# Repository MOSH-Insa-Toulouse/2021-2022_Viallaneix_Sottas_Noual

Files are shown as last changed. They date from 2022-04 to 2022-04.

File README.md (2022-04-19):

# 2021-2022_Viallaneix_Sottas_Noual MOSH Project 2022
Granulometric sensor

# Informations générales
> Ce projet s'inscrit dans le cadre de l'UF _"Du capteur au banc de test en open source hardware"_.
> Le cœur du projet bat sur la fréquence de la **LOW TECH**. Nous partirons de la fabrication d'un capteur granulométrique élaboré à partir d'une feuille de papier sur laquelle une couche de carbone sera déposée à l'aide d'un crayon à papier (panel de dureté entre HB et 9B) selon un motif prédeterminé. À ce corps d'épreuve, deux électrodes insérées aux extrémités du motif permettront la circulation d'un courant. Une déformation du capteur entraînera une variation du courant mesurable par un système d'acquisition de données. Les enjeux du projet sont donc multiples!
* **Physique** : sur les propriétés d'un capteur granulométrique
* **Technique** : sur la conception et le développement d'un système d'acquisition
* **Exploratoire** : par l'utilisation des outils et concepts de l'Open Source Hardware.
* **Se construire une composante _low-tech_  de l'ingénieur que nous serons** : en s'interrogeant sur les attentes d'une société en mutation, en posant un regard critique sur la notion de progrès technique et sa finalité.

low-tech

# Ce que fait ce projet 

> La finalité du projet est de pouvoir estimer les forces et faiblesses de ces capteurs low-tech. Pour cela nous allons devoir les tester, déterminer leurs caractéristiques et leur limites d'utilisations.
> Pour y parvenir, nous allons concevoir un banc de mesures qui nous permettra, dans un premier temps, d'étalonner les capteurs (leurs sensibilités varient en fonction de la dureté) puis, dans un deuxième temps, de les éprouver dans des conditions et durées d'utilisation controlées.
> Les jeux de données issues de ces tests vont devenir rapidement conséquents et il sera utile de prévoir les scripts et la visualisation en sortie du banc de test et étalonnage. 
> La composante **étalonnage** du banc permet de détérminer la sensibilité un capteur de sensibilité inconnue. La composante **test** permet de soumettre le capteur à des séries de flexion/déflexion fonction d'un angle compris entre -85 et +85 degrés par rapport à la position d'équilibre.
> Dans la suite du projet le capteur désignera le corps d'épreuve et le banc de test permettant l'acquisition des données.

***
## Les axes du projets
* [Présentation du capteur granulométrique](#présentation-du-capteur-granulométrique)
* [Acquisition des données](#acquisition-des-données)
  * [Carte Arduino](#la-carte-arduino)
  * [Étude du circuit électrique](#le-conditionneur)
    * [Partie 1: Mesure d'un très faible courant avec l'aide d'un micro-contrôleur](#partie-1-mesure-dun-très-faible-courant-avec-laide-dun-micro-contrôleur)
       * [Vérification avec la Datasheet de l'AOP](#vérification-avec-la-datasheet-de-laop)
    * [Partie 2: Mise en oeuvre du filtrage du signal](#partie-2-mise-en-oeuvre-du-filtrage-du-signal)
    * [Schéma du circuit électronique final](#schéma-du-circuit-électronique-final)
    * [Partie 3: Simulations sous *LTSpice*](#partie-3-simulations-sous-ltspice)
  * [Code Arduino du système](#code-arduino-du-système)
  * [Application sur Android](#application-sur-android)
* [Réalisation du PCB](#réalisation-du-pcb)
   * [Partie 1: Conception de la schématique et des connexions entre les composants électroniques](#partie-1-conception-de-la-schématique-et-des-connexions-entre-les-composants-électroniques)
   * [Partie 2: Conception du PCB](#partie-2-conception-du-pcb)
   * [Partie 3: Soudure des composants sur le PCB et premiers tests](#partie-3-soudure-des-composants-sur-le-pcb-et-premiers-tests)
* [Banc de tests](#banc-de-tests)
* [Measurement System Analysis](#measurement-system-analysis)
* [Crédits](#auteurs)

***

### Présentation du capteur granulométrique
> Le capteur sélectionné dans le cadre de ce projet est un dépôt de graphite sur un papier, effectué à l’aide d’un crayon plus ou moins gras. 
Nous utiliserons pour cela la résistivité du graphite, qui est suffisamment faible pour laisser circuler un courant mesurable. Néanmoins, avec cette résistivité de 8 µΩ.m (contre 0,017 µΩ.m pour le cuivre), il faudra utiliser un montage amplificateur dans notre banc de test.

> Le dépôt de graphite effectué sur le papier sera alors représentatif de la flexion que ce dernier subit : les grains de graphite jouent le rôle de conducteur mais leur éloignement variera selon la flexion, et va donc influencer la résistance mesurée.

<div align="center">
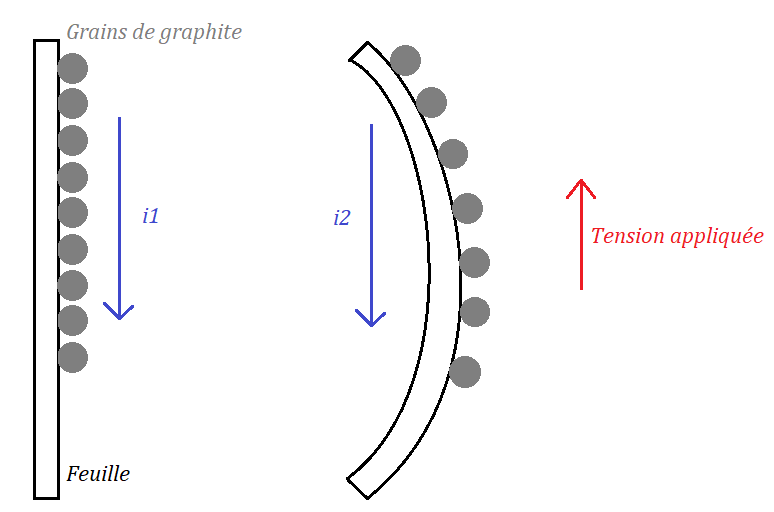
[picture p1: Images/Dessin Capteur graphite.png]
</p>

**Figure 1: Première description schématique d'une mesure sur le capteur de graphite**

<div align="left"></p>

> Dans l’exemple ci dessus, on mesurera pour une même tension appliquée que:

<div align="center">
</p>

<div align="left"></p>

> L’intérêt de ce capteur se situe dans son aspect low-tech qui lui permet d’être facilement produit, mais pas uniquement :  la vaste gamme de dureté des mines de crayon (H, F, HB, B) offre un large choix pour la résistivité du dépôt.
En effet, la dureté d’une mine correspond à ses proportions de graphite et d’argile. Le graphite est, par exemple, plus présent dans un crayon dit « gras » de type B que dans un crayon de type H. Ainsi, nous disposons assez simplement d’un large panel de capteurs pour éventuellement les comparer à l’aide du banc de tests.

(#### Propriété d'un système granulaire)
### Acquisition des données
#### La carte Arduino

Dans notre projet, nous allons utiliser la carte Arduino UNO possédant le microcontrôleur ATMega328. 

<div align="center">
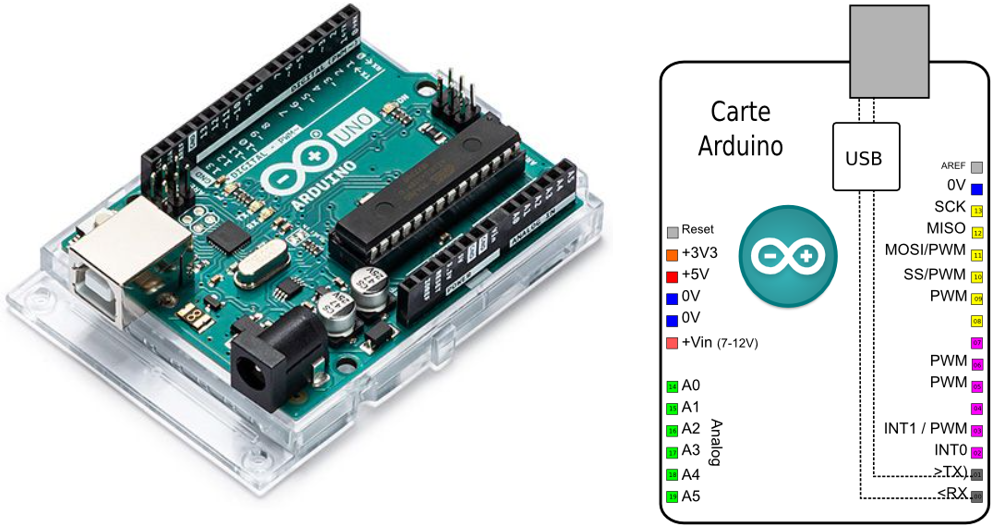
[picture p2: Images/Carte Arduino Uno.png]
</p>

**Figure 2: Illustration de la carte Arduino UNO et Brochage de la carte Arduino**

<div align="left"></p>

Elle dispose de 6 entrées analogiques et de 14 broches numériques d'entrées/sorties. 
Pour pouvoir l'utiliser, on a juste à la connecter directement à l'ordinateur via le câble USB. 

La carte Arduino UNO possède les caractéristiques suivantes: 

* **Résolution**: 10 à 12 bits (1024 à 4096 points)
* **Pleine échelle (VRef)**: de 1.1 V à 5.0 V
* **Impédance de source max**: 1 kΩ à 10 kΩ
* **Fréquence d'échantillonnage**: 15 kHz maximale

#### Le conditionneur

#### Partie 1: Mesure d'un très faible courant avec l'aide d'un micro-contrôleur
L’objectif étant d’extraire l’information utile du capteur ayant un très faible courant (environ 100 nA), le montage électrique doit être adapté de manière à mesurer des courants faibles. Selon les caractéristiques techniques du microcontrôleur Arduino (cf Datasheet), on ne peut pas mesurer directement de très faibles courants en raison de l’impédance de source (environ égale à quelques kOhms). Il est donc nécessaire d’utiliser un circuit amplificateur transimpédance composé d’un amplificateur opérationnel AOP pour convertir un courant issu du capteur en une tension mesurable par le CAN (Convertisseur Analogique-Numérique) de l’Arduino UNO.

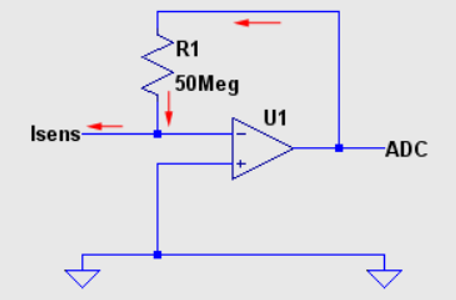
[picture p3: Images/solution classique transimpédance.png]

<div align="center"></p>
  
**Figure 3: Montage de transimpédance (ou convertisseur courant-tension)**
  
<div align="left"></p>

L’inconvénient d’un montage classique de transimpédance est qu’il nécessite une grande résistance pour amplifier le signal et que la tension d’alimentation du capteur doit être négative. On peut donc ajouter un autre étage inverseur à la suite du premier montage : 

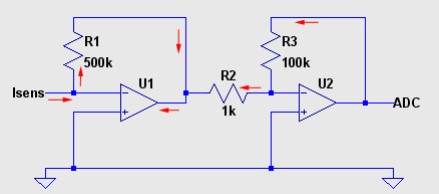
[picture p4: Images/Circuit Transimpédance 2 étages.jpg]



<div align="center"></p>
  
**Figures 4 et 5: Ajout d'un étage inverseur sur le montage de transimpédance et Calcul du gain du second montage**

<div align="left"></p>

Dans le montage ci-dessus, le gain du second étage étant négatif compte-tenu de son caractère inverseur (`cf Figure 3`), la résistance R1 du premier étage n’a plus besoin d’avoir une grande valeur. De plus, l’alimentation du capteur est donc positive grâce au second montage inverseur du fait des produits des gains de deux étages. 

Pour plus de simplicité, on a choisi un montage en prenant un seul AOP dans le montage.
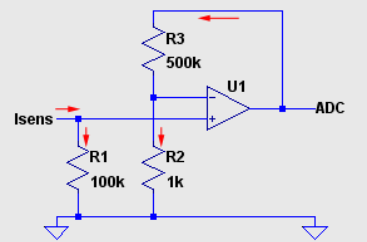
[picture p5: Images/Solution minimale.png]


<div align="center"></p> 

**Figure 6: Solution simplifiée pour le montage transimpédance**



**Figure 7: Calcul de la tension aux bornes de R1**

<div align="left"></p>
  
En calculant la tension aux bornes de la résistance R1, on obtient une tension environ égale à 10 mV d'après la `Figure 4`.

Il s’agit d’une valeur importante pour le choix de l’AOP notamment pour l'effet de l’offset du signal d’entrée. 
Le Gain de ce montage et la Tension de sortie ADC sont décrits dans les calculs ci-dessous : 




<div align="center"> </p>
  
**Figure 8: Calculs du gain du montage et de la tension de sortie**

<div align="left"></p>
  
Si on a un courant nul en entrée, on veut alors obtenir une tension ADC nulle en sortie, cela implique qu’il n’y ait pas de dérives en tension de la part de l’AOP.
Les principales contraintes pour le choix de l’amplificateur opérationnel sont le faible courant d’entrée et un très faible offset de tension devant être négligeable devant 10mV (tension aux bornes de R1).

##### Vérification avec la Datasheet de l'AOP

Selon les données de la [Datasheet](LTC1050C.pdf) de l'AOP 1050C, on constate qu'il possède un faible offset de tension d'environ 5μV au maximum et un très faible drift pour l'offset de tension à environ 0.05μV/°C. Cela indique la bonne stabilité de l'amplificateur opérationnel. Par comparaison, les AOP utilisés traditionnellement en salle de TP possèdent un offset autour de 5mV, une valeur 1000 fois plus grande que celle du 1050C.
En comparant la tension d'entrée (autour de 10mV `cf Figure 5`), on constate que l'offset de 5μV est très faible.
De plus, on peut remarquer que cet AOP possède un mode commun incluant la masse ce qui correspond à notre montage électrique.
  
<div align="center"></p>
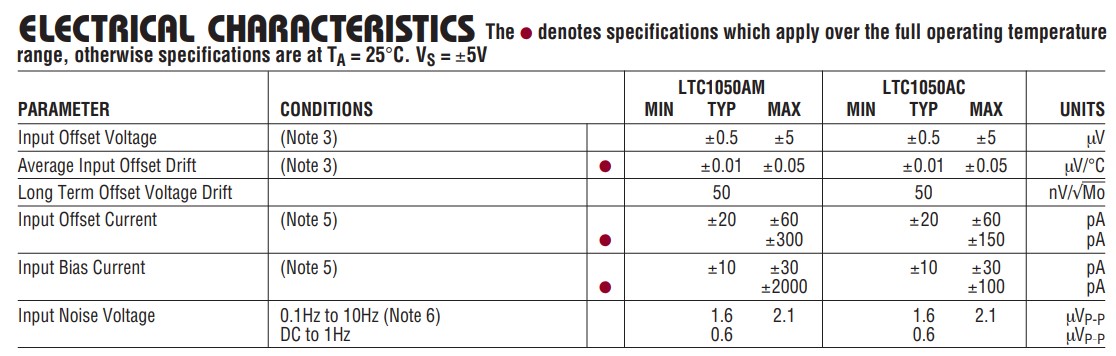
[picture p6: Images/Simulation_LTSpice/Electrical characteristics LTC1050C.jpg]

  
**Figure 9: Extrait de la datasheet dans la partie Electrical Characteristics**

<div align="left"></p>
  
Enfin, on constate que le courant de polarisation en entrée (Input Bias Current) est au maximum égale à 30pA, cela convient car nous effectuons des mesures de courant autour de 100nA. Il faut que le courant Isense `cf Figure 4` soit très faible devant 100nA et le reste du courant passe dans la résistance R1. 
En respectant les différentes conditions énoncées précédemment, l'AOP 1050C est adapté pour notre circuit électronique.

#### Partie 2: Mise en oeuvre du filtrage du signal

Étant donné que ce montage est très sensible aux signaux parasites (50Hz, horloge du microcontrôleur Arduino, Bluetooth entre autres), on doit mettre en œuvre un filtrage passe-bas pour limiter les perturbations du signal.
D’une part, il faut appliquer un filtre passif en entrée pour limiter les perturbations de type radiofréquences pouvant conduire à un excès de bruit dans l’ADC.
Ensuite, on applique un filtre actif au niveau de l’amplificateur opérationnel pour augmenter l’efficacité de l’échantillonnage du signal. 
À la sortie de l’AOP, on utilise un dernier filtre passif pour retirer le bruit sur le traitement du signal et les phénomènes de repliement de spectre (aliasing). 

En intégrant les différents filtres, le montage ressemble à ceci : 

<div align="center"></p>
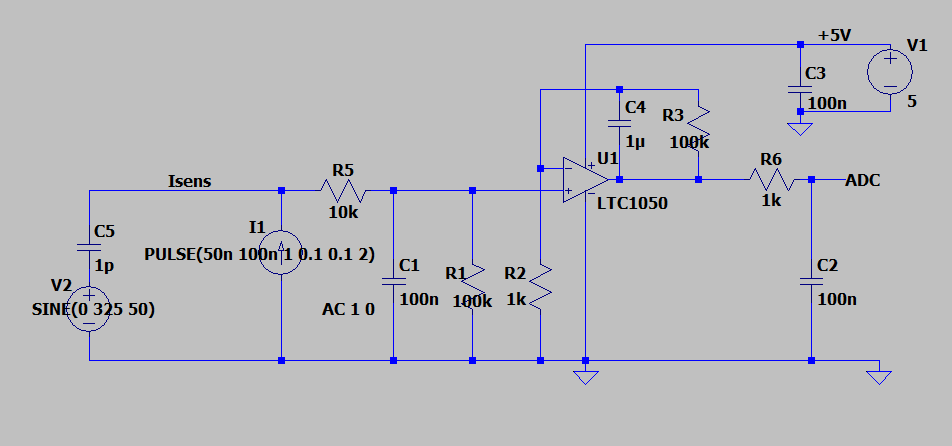
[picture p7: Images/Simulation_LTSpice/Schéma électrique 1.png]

  
**Figure 10: Schéma du montage électrique avec les différents filtres**

<div align="left"></p>

On distingue 3 différents filtres où nous avons cherché pour chacun la fréquence de coupure et son rôle principal pour le filtrage : 

<div align="center"></p>
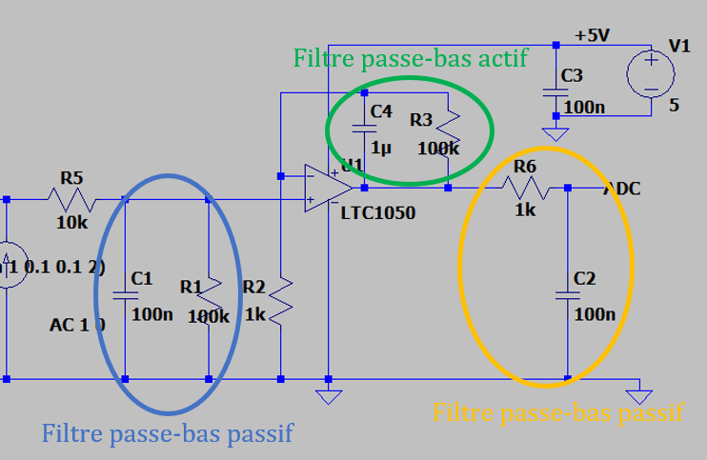
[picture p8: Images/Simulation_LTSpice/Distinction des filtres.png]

  
**Figure 11: Identification des différents filtres dans le montage**

<div align="left"></p> 
 
Tout d'abord, le filtre passe-bas passif, placé à l'entrée de l'AOP, est constitué de R1(100kΩ) et C1(100nF). Il possède une fréquence de coupure théorique environ égale à 16Hz `cf Figure 7` . Il permet donc de filtrer les perturbations et les excès de bruit en courant sur la forme du signal d'entrée. 


<div align="center"></p> 

**Figure 12: Calcul de la fréquence de coupure du filtre passif (R1 et C1)**

<div align="left"></p>

Ensuite, le filtre passe-bas actif, placé entre l'entrée et la sortie de l'AOP, est constitué de R3(100kΩ) et C4(1μF) en parallèle. Ce dernier possède une fréquence de coupure théorique environ égale à 1.6Hz `cf Figure 8`. Son rôle principal est de supprimer la composante parasite de 50Hz (du fait du couplage capacitif avec la tension 230V) qui perturbe significativement le signal `cf Figure XX`.


<div align="center"></p>

**Figure 13: Calcul de la fréquence de coupure du filtre actif (R3 et C4)**

<div align="left"></p>

Enfin, le filtre passe-bas passif, placé à la sortie de l'AOP, est constitué de R6(100kΩ) et C2(100nF). Il possède une fréquence de coupure théorique environ égale à 1.6kHz `cf Figure 9`. En sachant que la fréquence d'échantillonnage du micro-contrôleur est environ égale à 15,4kHz, il faut respecter la condition d'échantillonnage de Shannon à savoir:  

<div align="center"></p> 

</p>
</p>
</p>

**Figures 14: Calcul de la fréquence de coupure du filtre passif (R6 et C2) et Vérification de la condition d'échantillonnage de Shannon**

<div align="left"></p>

Selon les calculs, on respecte bien la condition d'échantillonnage de Shannon `cf Figure ci-dessus`, le filtre permet de limiter les effets de repliement de spectre (rôle d'anti-aliasing) et de manière générale, le bruit lors du traitement du signal. 

#### Schéma du circuit électronique final
> Voici un première proposition du schéma électrique
  
<div align="center"></p>


**Figure 15: Premier schéma du montage électronique**

<div align="left"></p>
  
Dans ce schéma, nous simulons le bruit en courant à l'entrée en mettant une capacité à côté du générateur de tension. On a ajouté une capacité C3 pour filtrer le bruit de la source d'alimentation.
  
> On propose une optimisation du montage électronique en simulant le capteur de graphite `cf Figure ci-dessous`
  
<div align="center"></p>
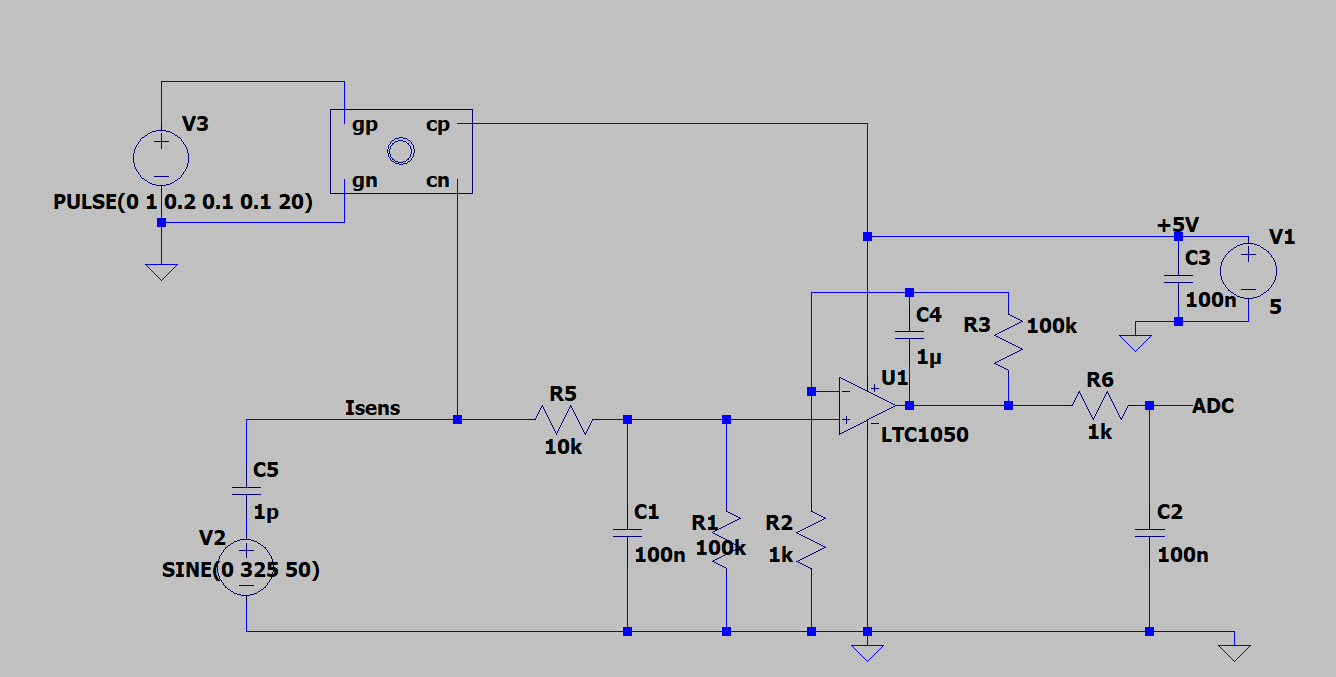
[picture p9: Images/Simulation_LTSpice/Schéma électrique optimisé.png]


**Figure 16: Schéma électrique optimisé**

<div align="left"></p>
  
Nous avons simulé notre capteur de graphite (cf rectangle en haut à gauche de la `figure précédente`). 
> Commentaires à ajouter

#### Partie 3: Simulations sous *LTSpice*
  
On vérifie les conditions optimales de fonctionnement du montage électronique en effectuant différentes simulations sur le logiciel *LTSPice* `cf figures ci-dessous`.

<div align="center"></p>
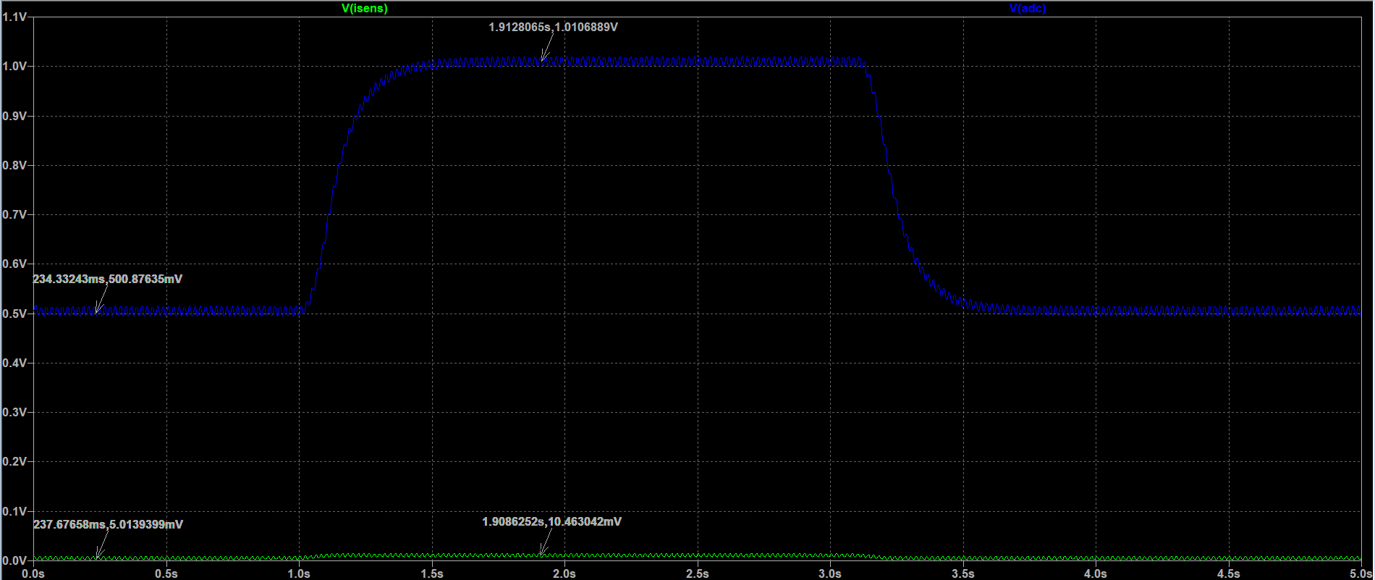
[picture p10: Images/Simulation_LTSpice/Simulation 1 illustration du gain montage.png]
</p>

**Figure 17: Vérification du gain d'amplification du signal environ égal 100**
  
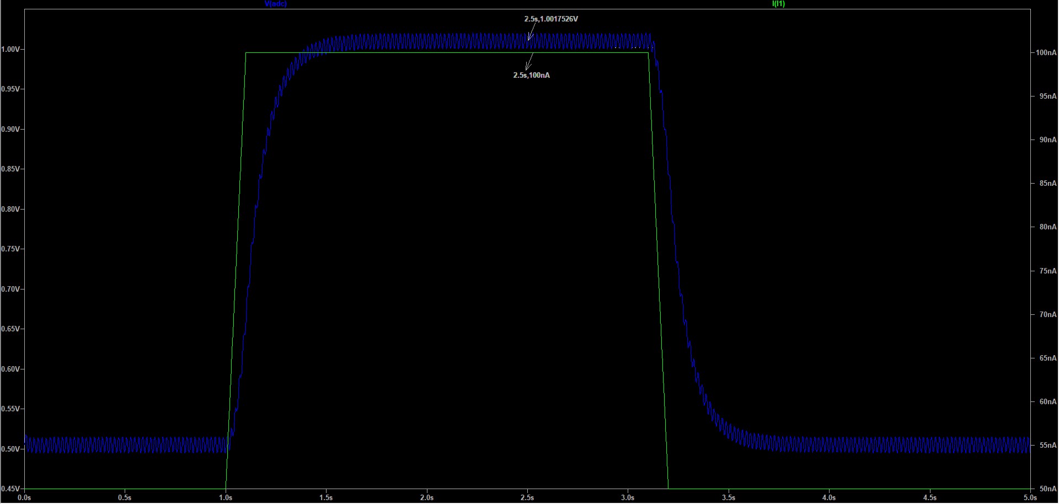
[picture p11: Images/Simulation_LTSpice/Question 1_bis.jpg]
</p>

**Figure 18: Vérification du la tension de sortie du montage avec un courant d'entrée égal à 100nA**

<div align="left"></p>
  
Pour l'illustration graphique du gain du montage général, on distingue qu'il y a bien 3 filtres dans le circuit électronique grâce aux différentes variations du terme de phase (courbe en traits en pointillés `cf Figure ci-dessous`).

<div align="center"></p>
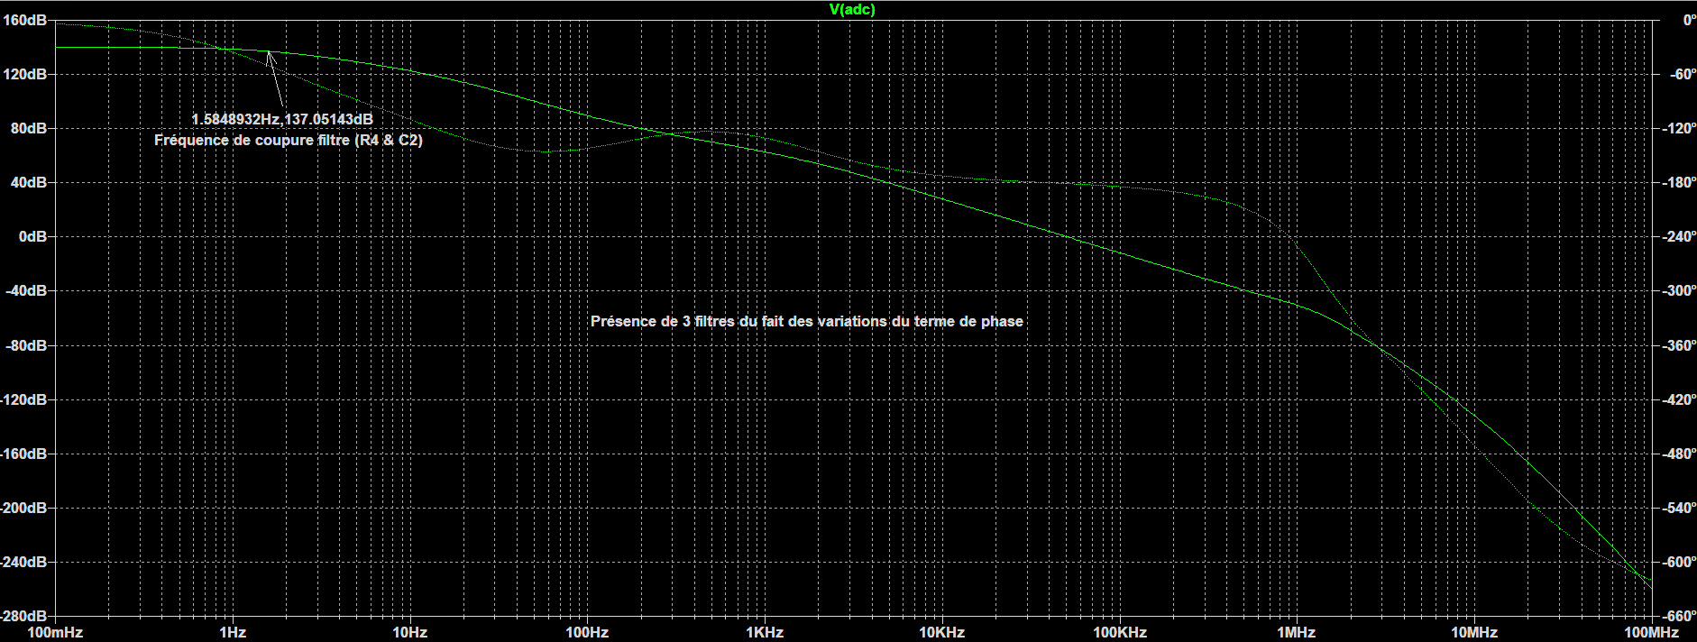
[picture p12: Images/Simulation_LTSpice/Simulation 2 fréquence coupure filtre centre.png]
</p>

**Figure 19: Identification graphique des 3 filtres**

<div align="left"></p>

> On vérifie graphiquement la fréquence de coupure de chaque filtre en effectuant une simulation fréquentielle (AC Sweep):

Pour le premier filtre à l'entrée de l'AOP (R1 et C1):
<div align="center">
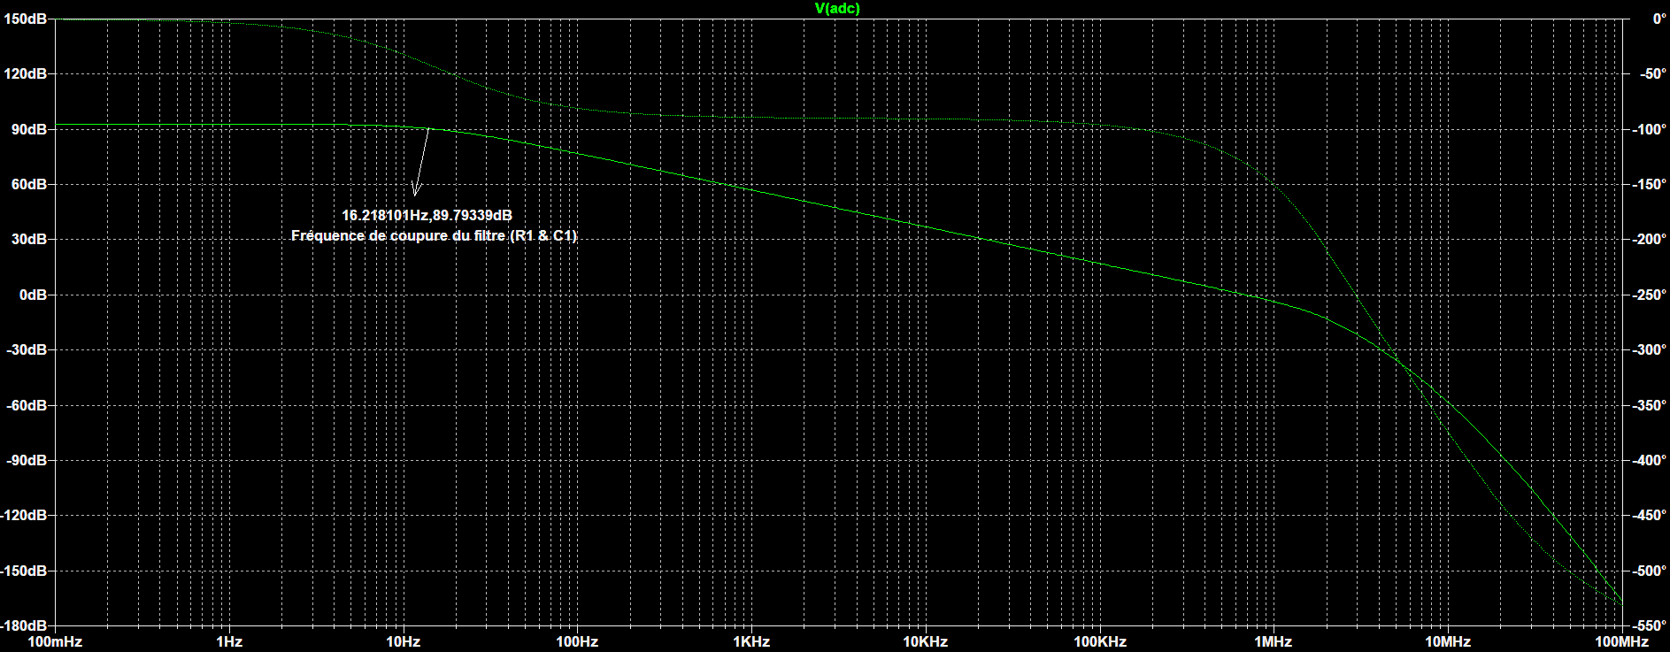
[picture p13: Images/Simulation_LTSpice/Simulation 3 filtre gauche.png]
</p>

**Figure 20: Illustration graphique de la fréquence de coupure du filtre (R1 et C1)**

<div align="left"></p>
  
Pour le second filtre entre l'entrée et la sortie de l'AOP (R3 et C4) et le dernier filtre à la sortie (R6 et C2):
  
<div align="center">
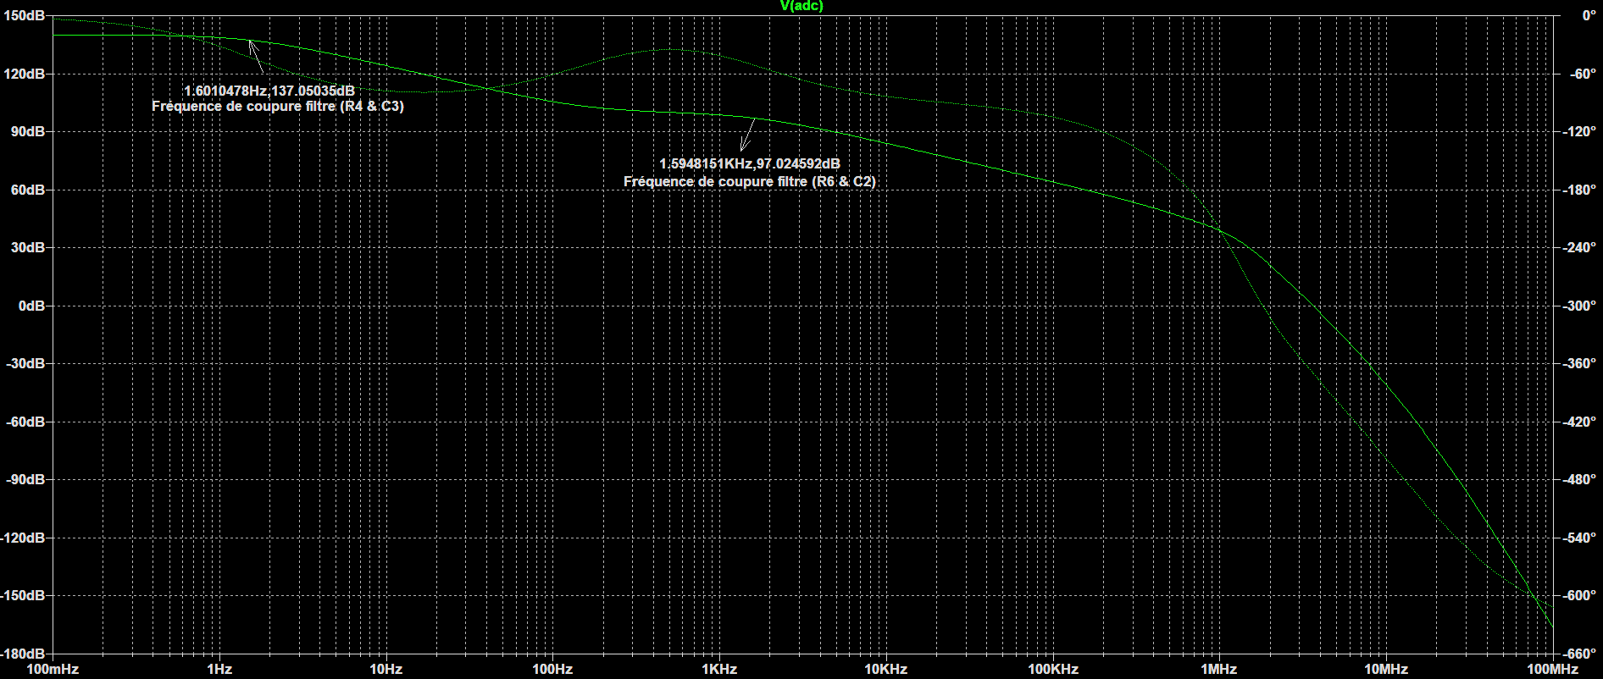
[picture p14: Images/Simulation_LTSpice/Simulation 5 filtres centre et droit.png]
</p>

**Figure 21: Illustration graphique des fréquences de coupure des deux filtres passe-bas**

<div align="left"></p>

> On vérifie l'incidence du courant d'entrée de l'amplificateur sur la tension de sortie par une simulation temporelle:

<div align="center">
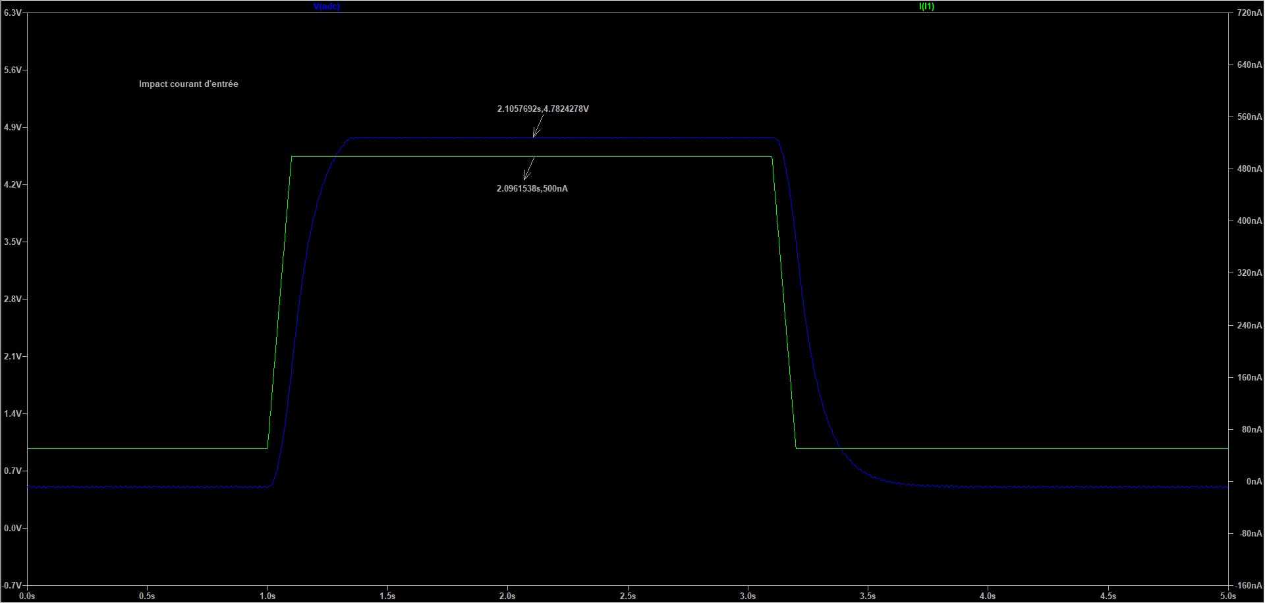
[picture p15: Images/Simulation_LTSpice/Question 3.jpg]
</p>

**Figure 22: Illustration graphique de l'incidence du courant d'entrée sur la tension de sortie**

<div align="left"></p>
  
On peut remarquer dans cette image qu'à partir d'une valeur de 500nA pour le courant d'entrée, on obtient une tension pouvant saturer le convertisseur analogique-numérique de l'Arduino. 

> On observe graphiquement l'atténuation globale du signal d'un bruit en courant de 50 Hz ainsi que celle associée à un bruit en courant à la fréquence de repliement de spectre autour de 7 kHz. 

<div align="center">
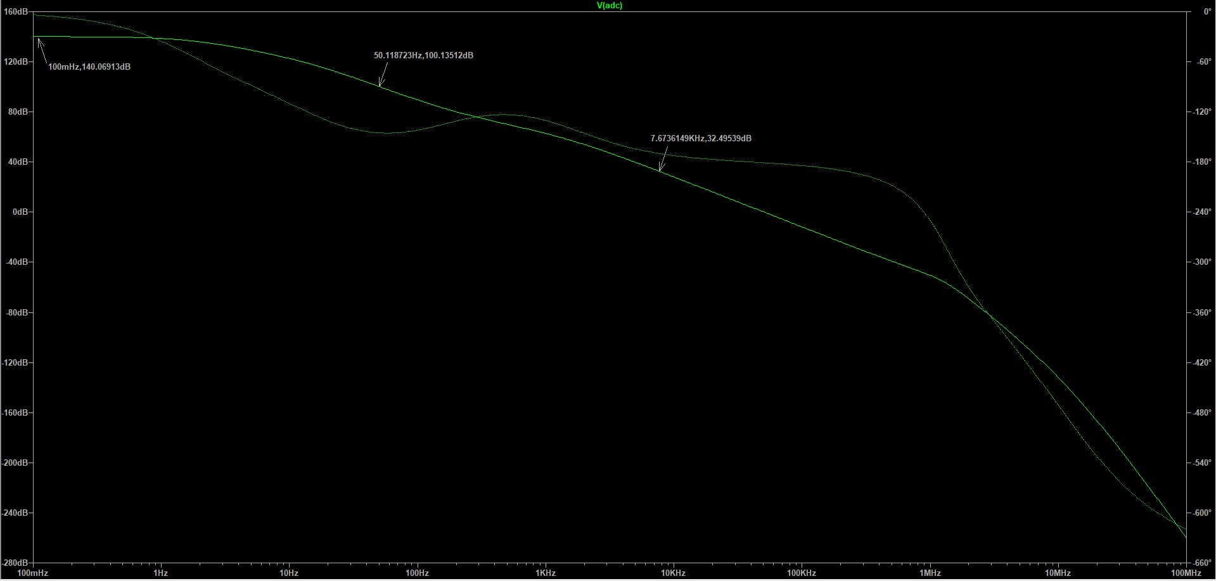
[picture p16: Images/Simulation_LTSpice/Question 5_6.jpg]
</p>
 


**Figures 23 et 24: Illustration graphique de l'atténuation du signal d'un bruit en courant pour deux fréquences spécifiques et calculs des atténuations**

<div align="left"></p>

Comme on peut le voir avec les calculs précédents, on constate qu'il y a une atténuation en bruit de courant environ égale à 40dB pour une fréquence autour de 50Hz et elle est environ égale à 100 dB pour un bruit en courant au voisinage de la fréquence de repliement de spectre. Cela montre bien que le signal peut être fortement perturbé et atténué si on laisse la composante fréquentielle à 50 Hz et si on ne respecte la condition d'échantillonnage.   

### Code Arduino du système
<div align="center">
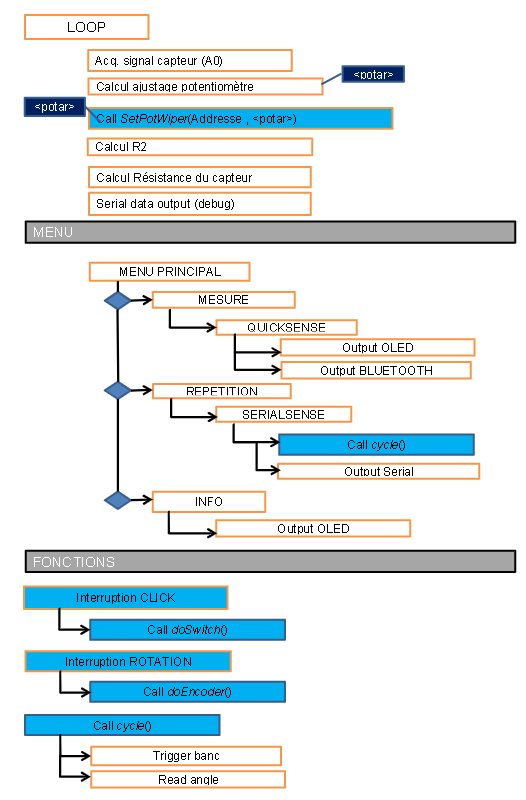
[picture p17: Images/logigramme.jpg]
</p>

**Figure 25: Logigramme de notre code Arduino**

<div align="left"></p>
  
Voici une présentation graphique de notre code Arduino.
  
### Application sur Android

L'application mobile associée au banc de test fonctionne avec un timer identique à celui du programme Arduino. L'utilisateur peut se connecter au module Bluetooth de son choix, puis vérifie que la connexion est bien établie avec un second bouton. Il peut ensuite lancer la mesure et afficher les résultats reçus sur un graphe en temps réel, afin de suivre l'évolution de la résistance du capteur. Le graphe reprend du début lorsque le balayage atteint le bout de l'écran, mais l'utilisateur peut le réinitialiser à sa guise avec un autre bouton. Enfin, la mesure peut être arrêtée en appuyant à nouveau sur le bouton qui l'a déclenché.

<div align="center"></p>
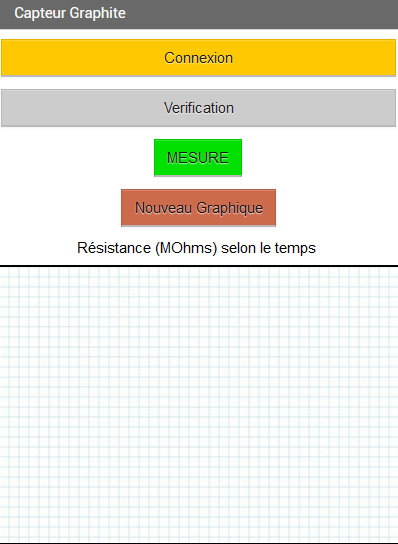
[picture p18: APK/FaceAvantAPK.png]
</p>

**Figure 26: Aperçu visuel de notre application**

<div align="left"></p>

<div align="center">
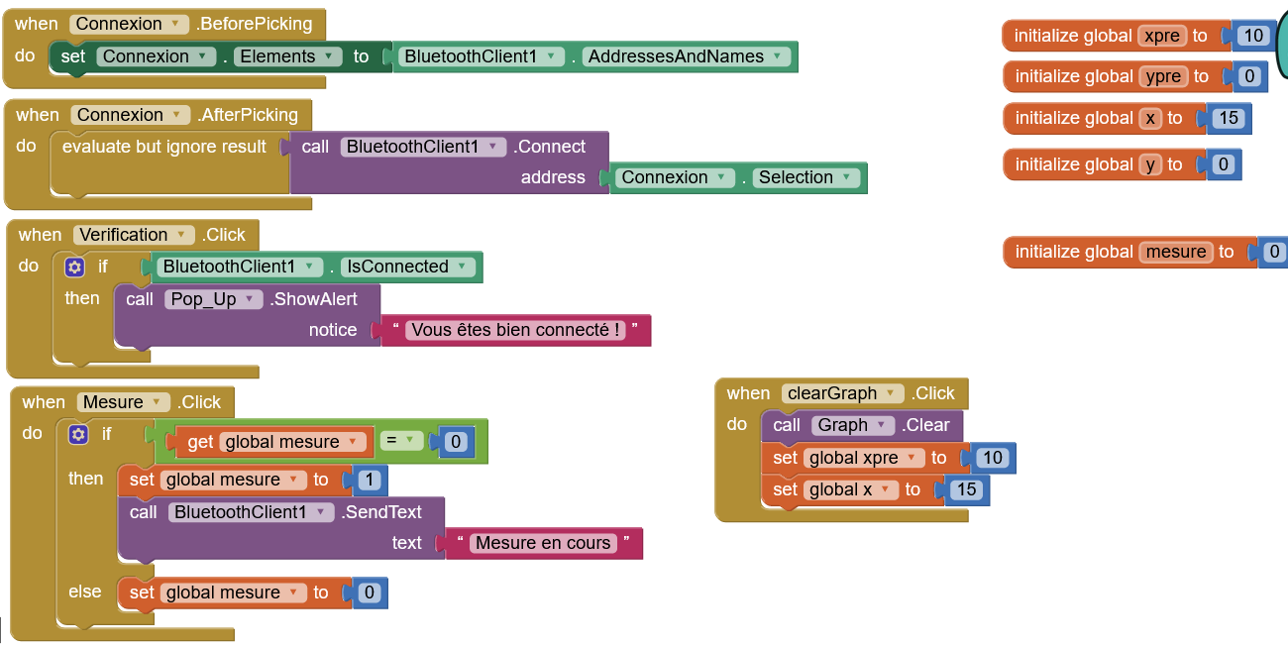
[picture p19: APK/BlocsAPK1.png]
</p>
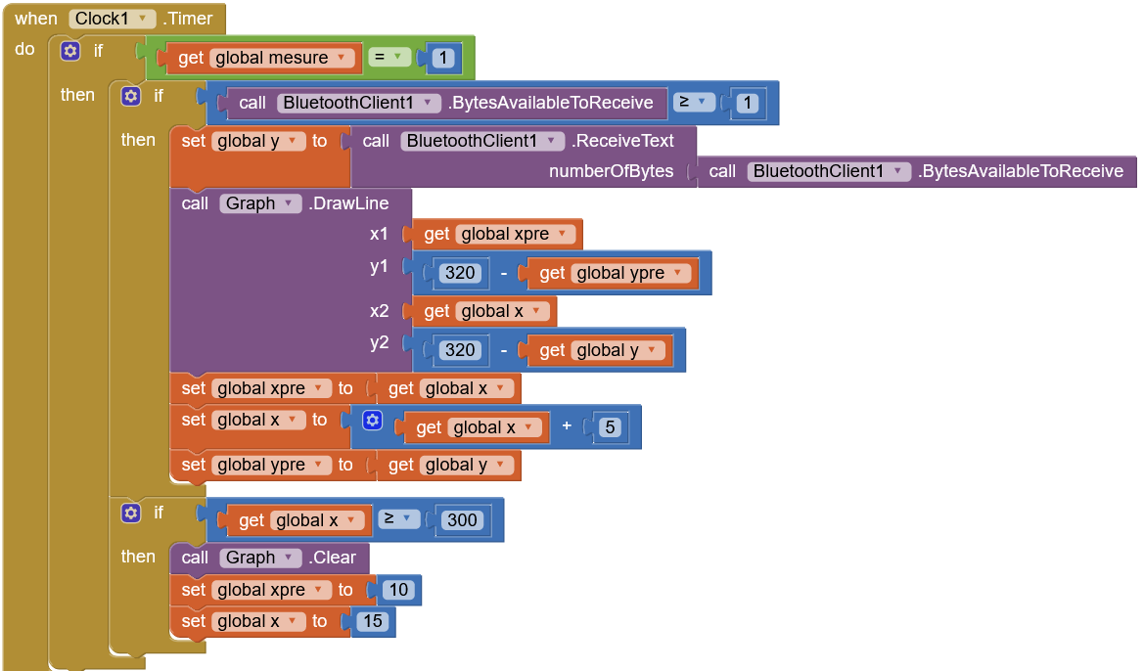
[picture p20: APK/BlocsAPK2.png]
</p>

**Figures 27 et 28: Extraits des blocs pour la réalisation de l'application Android sur *MIT App Inventor***

<div align="left"></p>   

### Réalisation du PCB

Après avoir réalisé les simulations sur *LTSpice*, nous avons conçu un premier modèle de PCB avec l'aide du logiciel *KiCAD*. 

#### Partie 1: Conception de la schématique et des connexions entre les composants électroniques

> Lors de cette étape, nous avons choisi un modèle basé sur l'Arduino UNO pour avoir les bonnes dimensions de la carte et les pins de connexion adéquats. Afin de réaliser précisément le PCB, nous avons dû concevoir certains composants électroniques nous-mêmes dans la partie Schématique (écran OLED, module Bluetooth, l'amplificateur LTC1050C, l'encodeur rotatoire et le potentiomètre digital)  `cf Figures ci-dessous`

<div align="center">
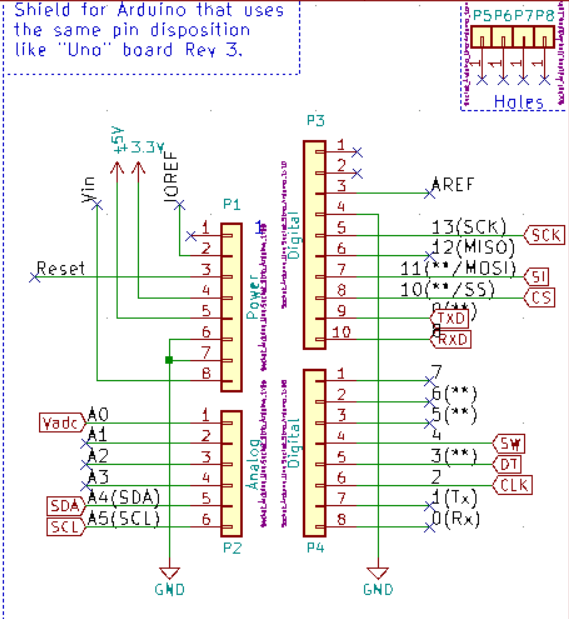
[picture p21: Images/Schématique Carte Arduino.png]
</p>

**Figure 29: Schéma des pins de connexion de la carte Arduino UNO **

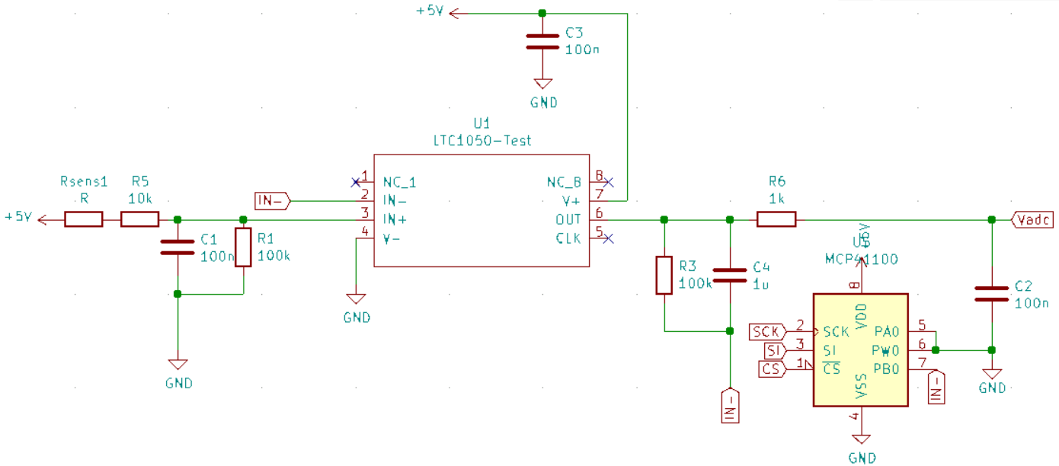
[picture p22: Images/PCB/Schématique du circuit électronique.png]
</p>
 
**Figure 30: Schéma du circuit électronique**
 
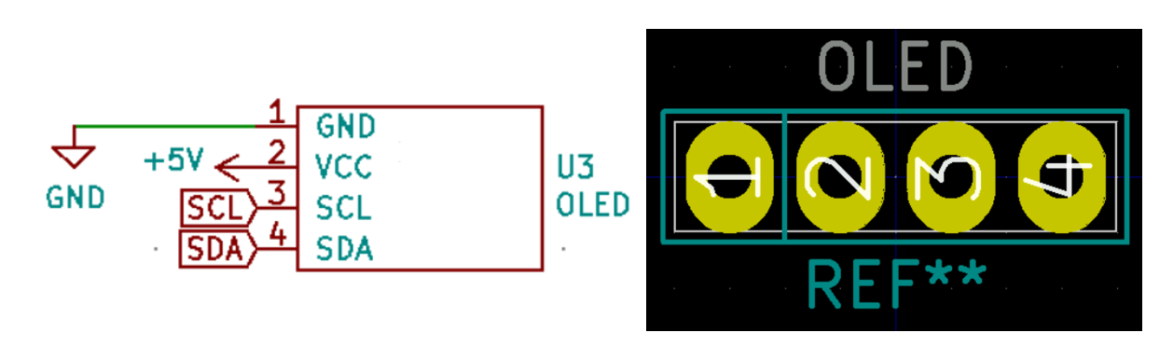
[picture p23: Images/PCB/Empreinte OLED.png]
</p>
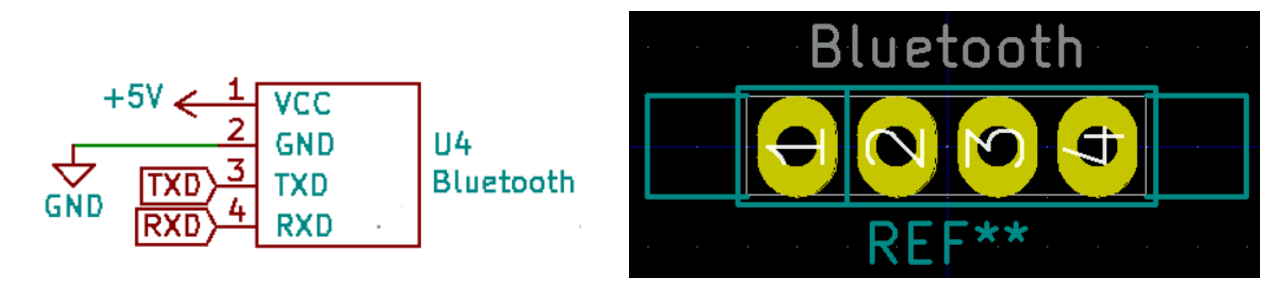
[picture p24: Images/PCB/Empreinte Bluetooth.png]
</p>
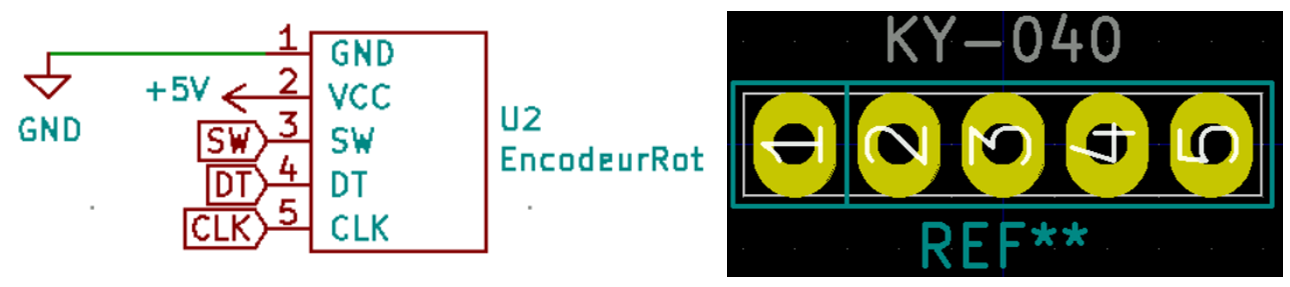
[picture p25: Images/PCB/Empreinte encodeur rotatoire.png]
</p>
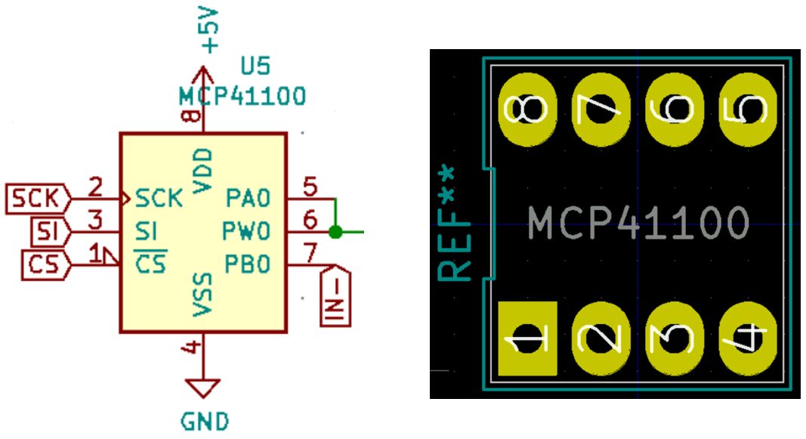
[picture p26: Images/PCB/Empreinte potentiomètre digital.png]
</p>

**Figures 31: Schémas et empreintes de chacun de nos composants électroniques (Écran OLED, BLuetooth, Encodeur rotatoire, Potentiomètre digital)**

<div align="left"></p>

#### Partie 2: Conception du PCB

> Dans cette partie, nous plaçons virtuellement les différents composants sur le PCB et nous effectuons toutes les connexions entre les pins de composants et ceux de la carte Arduino. Nos différents professeurs réferents (Mr Jérémie Grisolia et Mme Catherine Crouzet) nous ont indiqués les consignes à respecter pour la réalisation du PCB: 
  
* Largeur des pistes = 0.6 mm
* Largeur d'isolation des pistes = 0.9 mm
* Dimensions du trou pour l'écran OLED, le module Bluetooth et l'encodeur rotatoire = 2 mm * 2.5 mm
* Diamètre du via (trou entre la face avant et arrières du PCB) = 2 mm
* Taille du trou de perçage du via = 0.8 mm
* Taille du trou de perçage pour l'écran OLED, le module Bluetooth et l'encodeur rotatoire, l'AOP et le potentiomètre digital = 1 mm
* Dimensions du trou pour le support de l'AOP (pad n°1 rectangulaire et les autres pins sont ovales) = 2 mm * 2.5 mm
* Taille du trou de perçage pour les résistances et les capacités = 0.8 mm
  
<div align="center">
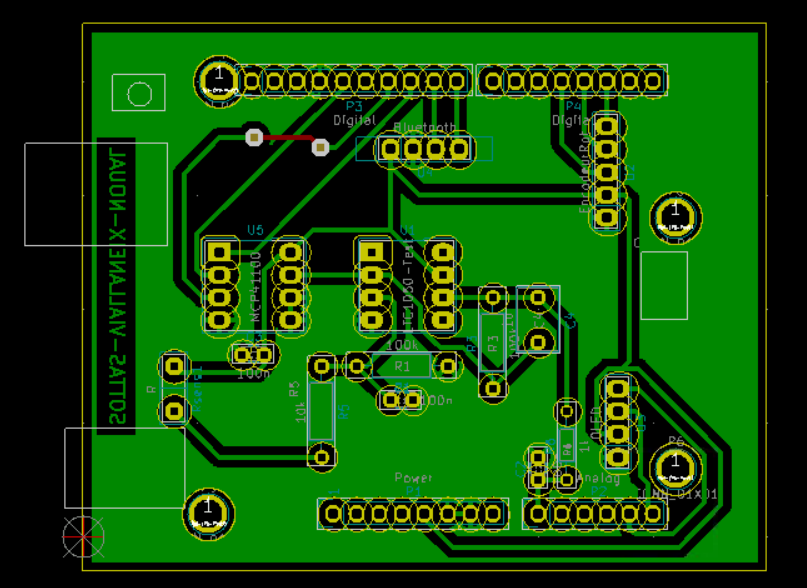
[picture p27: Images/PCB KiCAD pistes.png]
</p>

**Figure 32: Schémas des pistes sur le PCB**

<div align="left"></p>

<div align="center">
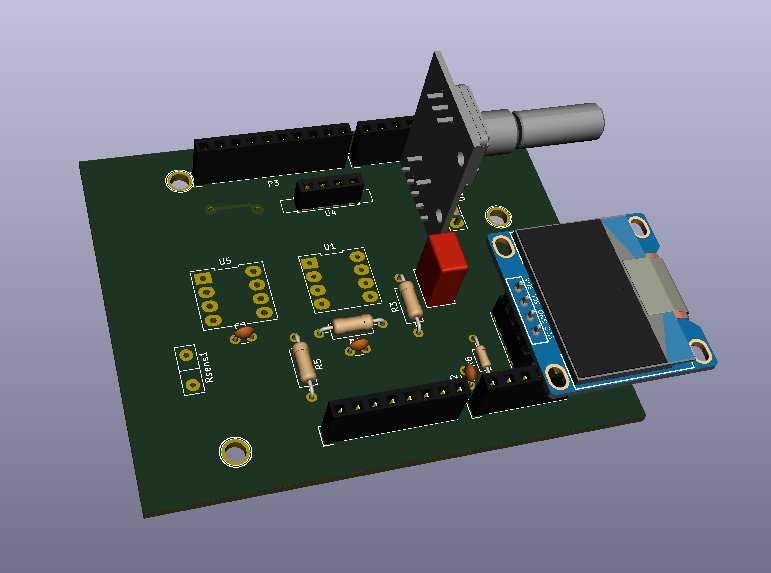
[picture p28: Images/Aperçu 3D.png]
</p>

**Figure 33: Schéma 3D des pistes sur le PCB**

<div align="left"></p>
  
Avec l'aide de Mme Catherine Crouzet, nous avons réalisé le PCB selon le protocole suivant:

* Insolation de la plaque de résine positive par photo-lithographie UV par contact avec un masque `cf Figure ci-dessous` imprimé sur un film transparent, provenant du logiciel *KiCAD*. Cette résine est choisie de telle manière à être sensible aux rayons UV.
Une fois l'insolation réalisée, la partie de la résine insolée est dissoute dans une solution de développeur. Le reste de la résine, étant protégé par le masque, reste intact. On observe l'apparition des pistes du circuit sur le PCB.
  
* Passage dans un bain de péroxyde de fer pour enlever les résidus de la piste de cuivre sur le PCB
  
* Nettoyage et Séchage de la plaque à l'eau naturelle

<div align="center">
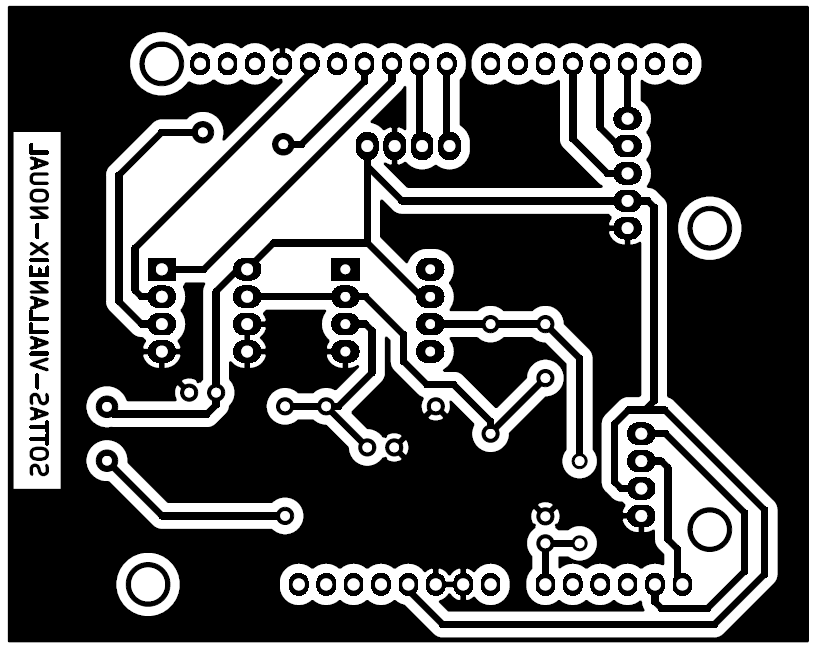
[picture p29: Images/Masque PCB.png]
</p>

**Figure 34: Masque imprimé du PCB sur un film transparent**

<div align="left"></p>

#### Partie 3: Soudure des composants sur le PCB et premiers tests
 
Uns fois le PCB réalisé, nous avons percé tous les trous des pins associés à chaque composant électronique puis nous avons soudé les différents composants et les broches latérales entre le PCB et la carte Arduino.

### Banc de tests

> Le but de ce banc de test est de déterminer la sensibilité du capteur, de voir l’évolution de cette dernière selon la répétition des flexions et de comparer ces données avec un capteur commercialisé "Flex-Sensor".

> Ce banc de test est composé d’un servomoteur pour une bonne précision sur les angles, ainsi que d’un support où l’on vient encastrer le capteur. Une roue où l’on positionne le bout du capteur est alors entraînée par le servomoteur et génère la flexion. Il est fait de plaques de contreplaqué superposées, qui ont été découpées au FabLab et il permet de garder le capteur le plus intact possible, car celui-ci n’est maintenu qu’aux deux extrêmités et non pas sur le dépôt de graphite lui-même.
L’utilisateur détermine au préalable le nombre de répétitions souhaité à l’aide de l’encodeur rotatoire placé sur le PCB. Il peut ensuite récupérer les données (angle, itération de la mesure, résistance lue) sur le moniteur série et les traiter dans un logiciel comme Rmarkdown, Python via l'interpréteur Spyder IDE ou Qtiplot.
Le capteur qui servira de référence comparative sera le Flex Sensor fourni dans le kit Arduino, qui possède déjà une datasheet.

> Nous avons élaboré un premier modèle en 2D ainsi qu'un modèle 3D de notre banc de tests: 
<div align="center"></p>

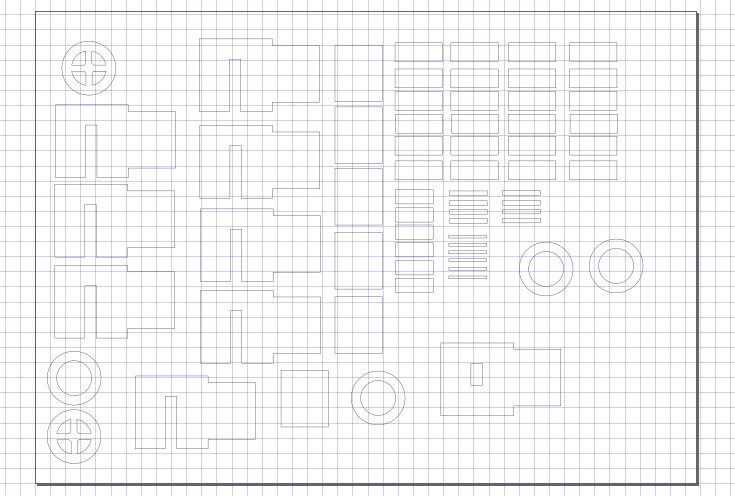
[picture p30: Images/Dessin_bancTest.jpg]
Dessin 2D du banc de tests Dessin 2D montage banc de test


**Figure 35: Dessin 2D du banc de test**

<div align="left"></p>
<div align="center"></p>

</p>

**Figure 36: Dessin 3D du banc de test sur *FreeCAD***

<div align="left"></p>

> Nous l'avons ensuite réalisé au FabLab avec l'aide d'une découpe laser: 

<div align="center">
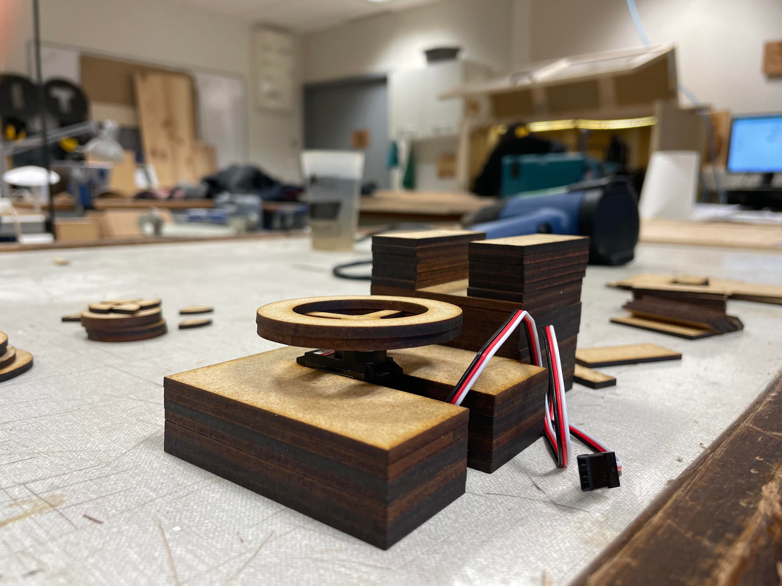
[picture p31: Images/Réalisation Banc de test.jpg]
</p>

**Figure 37: Réalisation du banc de test au FabLab**

<div align="left"></p>

Nous avons ensuite effectué les premiers tests sur notre banc de tests avec notre capteur: 

<div align="center">
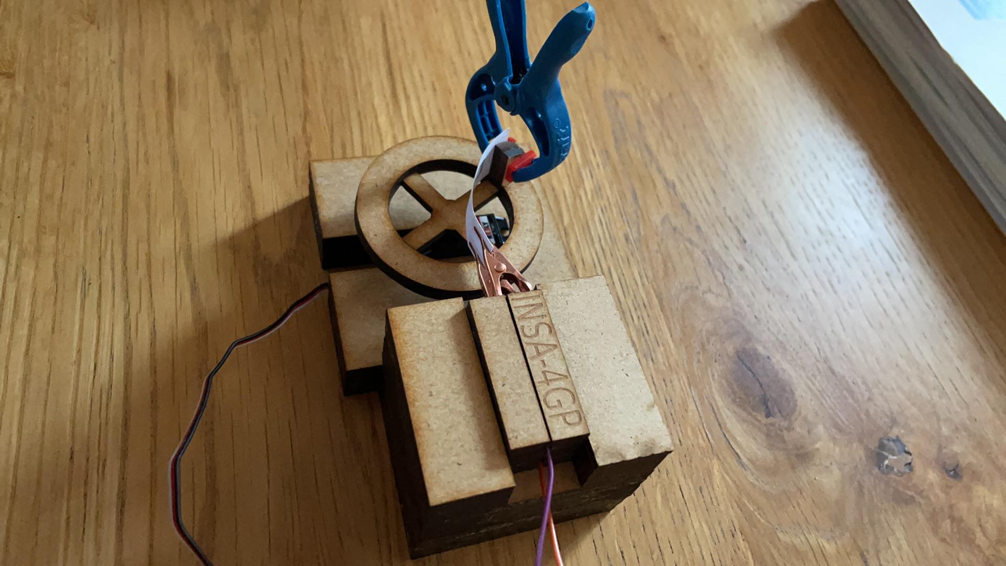
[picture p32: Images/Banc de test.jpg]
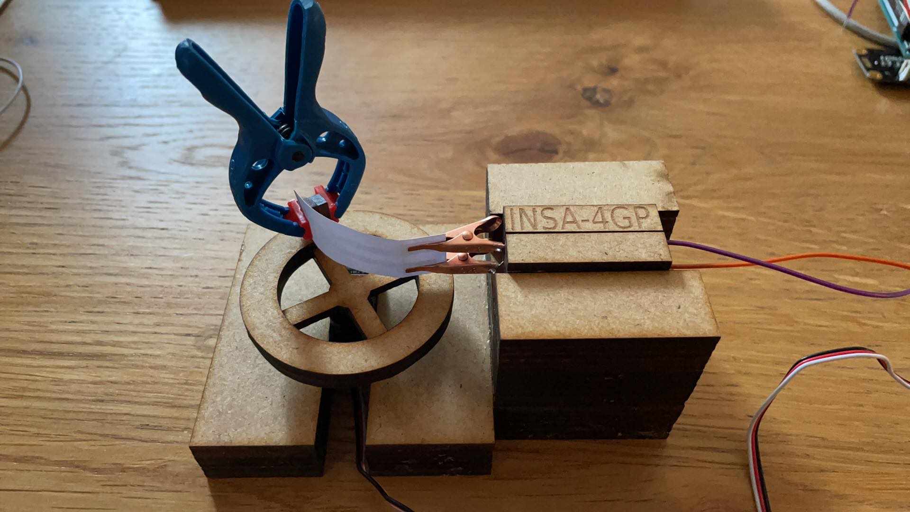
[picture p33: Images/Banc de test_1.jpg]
</p>

**Figure 38: Premiers tests avec notre banc de tests**

<div align="left"></p>

### Measurement System Analysis

### Auteurs

Arona SOTTAS, Léo VIALLANEIX et Raphaël NOUAL

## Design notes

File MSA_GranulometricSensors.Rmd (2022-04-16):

---
title: "Analyse du Système de Mesures"
author: "NOUAL R., SOTTAS A., VIALLANEIX L."
date: '2022-04-16'
output: 
  html_document: 
    fig_width: 10
    fig_height: 15
---

## Analyse du systeme de mesure
### Introduction

* Ce document est une préparation pour acceuillir les données du projets capteur granulométrique.
* Les calculs sont réalisé à l'aide du package SixSigma.
* Les données ont été prise à partir de ce document :  
[démarche iso 17025](http://www.demarcheiso17025.com/fiche005.html#d2)  
Cet étape à pour but de se familiariser avec la fonction ss.rr() de SixSigma qui permet d'implémenter la méthode R&R (Réptabilité et Reproductibilité).
Cet outils statistique permet de quantifier la performance d'un système de mesure en déterminant la contribution de la répétabilité, de la reproductibilité du sytème et celle de la variance de la variable d'intérêt du système de mesure par rapport à la variance totale de la mesure.
* Cette analyse nous donnera la capabilité du système.

### Méthodologie

La méthode décrite par la littérature demande les éléments suivants : 

* 2 à 3 opérateurs.  
* 10 pièces de test (les capteurs granulométriques dans notre cas).  
* 3 séries de mesure par capteur et par opérateur (soit un total de 90 mesures).  

### Variable d'intérêt

* La variable mesurée est la sensibilité du capteur granulométrique (ou R/R0).

### Le code

```{r}
# Import SixSigma package
library(SixSigma)

# Specify the factors for appraisals - Opérateurs dans notre cas
operateurs <- factor(rep(1:3, each = 30))

# Specify the factors for parts - les 10 capteurs de test
sensor <- factor(rep(rep(1:10, each = 3), 3))

# Specify the factors for replicates
run <- factor(rep(1:3, 30))
 
# Specify the measured variable
sensibilite <- c(45.08,45.1,45.09,44.94,44.97,44.93,45.08,45.11,45.13,44.97,45.02,45.01,44.92,44.95,45.01,45.03,45.06,45.05,45.24,45.36,45.31,45.16,45.16,45.1,45.2,45.2,45.24,45.07,45.1,45.05,45.01,45.04,45.02,44.92,44.95,44.95,44.95,45.11,45.11,45.01,44.93,45,44.95,44.99,44.97,45.04,45.06,44.99,45.12,45.21,45.32,45.12,45.13,45.13,45.06,45.19,45.24,45.02,45.05,45.09,45.04,45.07,45.07,44.92,44.97,44.91,45.1,45.12,45.11,45.02,44.99,44.99,44.99,44.97,44.95,45.07,45.03,45.02,45.26,45.29,45.28,45.13,45.13,45.14,45.19,45.17,45.16,45.1,45.1,45.09)

# Build data frame msa (measurement systeme analyse)
msa <- data.frame(operateurs, sensor, run, sensibilite)
#Aperçu du début et de la fin du dataframe
head(msa)
tail(msa)

# Perform Gage R&R Analysis 
my.rr <- ss.rr(var = sensibilite,
               part = sensor,
               appr = operateurs,
               data = msa,
               sigma = 5.15,
               alphaLim = 2,
               main = "Six Sigma Gage R&R Measure",
               sub = "Granulometric Sensors Project MSA")

# RESULTATS

```

### Discussions et conclusions

* **Reproductibilité**
* **Répétabilité**
* **Variabilité capteur**
* **Capabilité**

### Références

* www.demarcheiso17025.com
* Six Sigma with R, Statistical Engineering for Process Improvement, Emilio L.Cano, Javier M. Moguerza, Andrés Redchuck
* [Wiki](https://fr.wikipedia.org/wiki/Gage_R%26R)

Fin du document

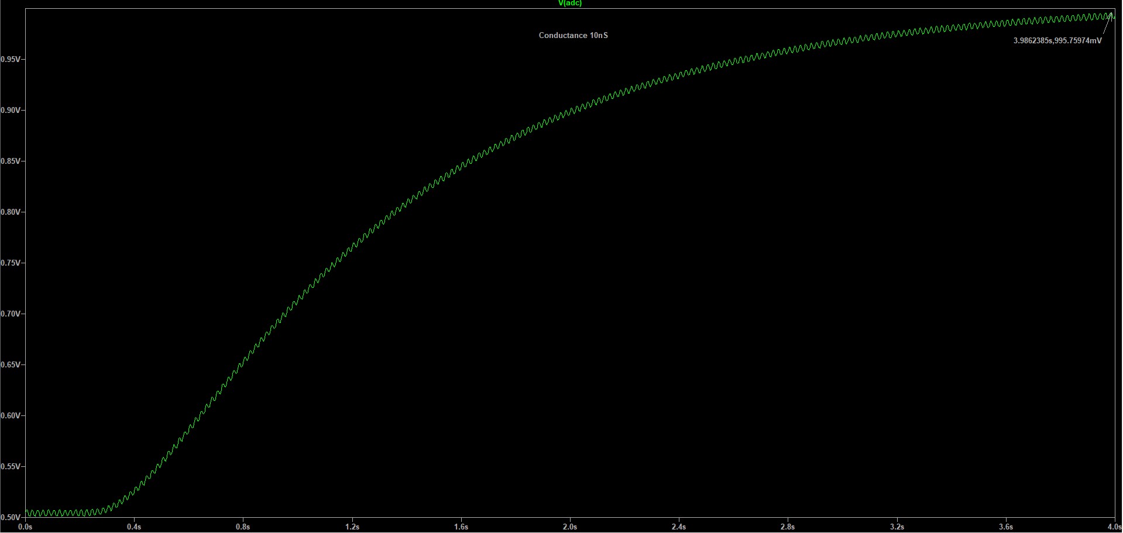
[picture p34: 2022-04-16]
Images/Simulation_LTSpice/Question 7_bis.jpg

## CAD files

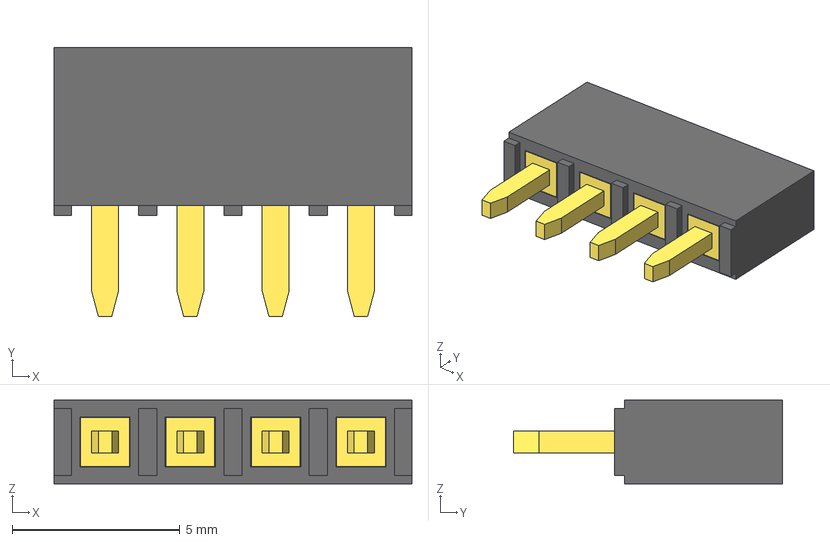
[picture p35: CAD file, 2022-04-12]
Shield/4-Pin Header - Female - 2.54mm.step
10.7 x 8.00 x 2.50 mm

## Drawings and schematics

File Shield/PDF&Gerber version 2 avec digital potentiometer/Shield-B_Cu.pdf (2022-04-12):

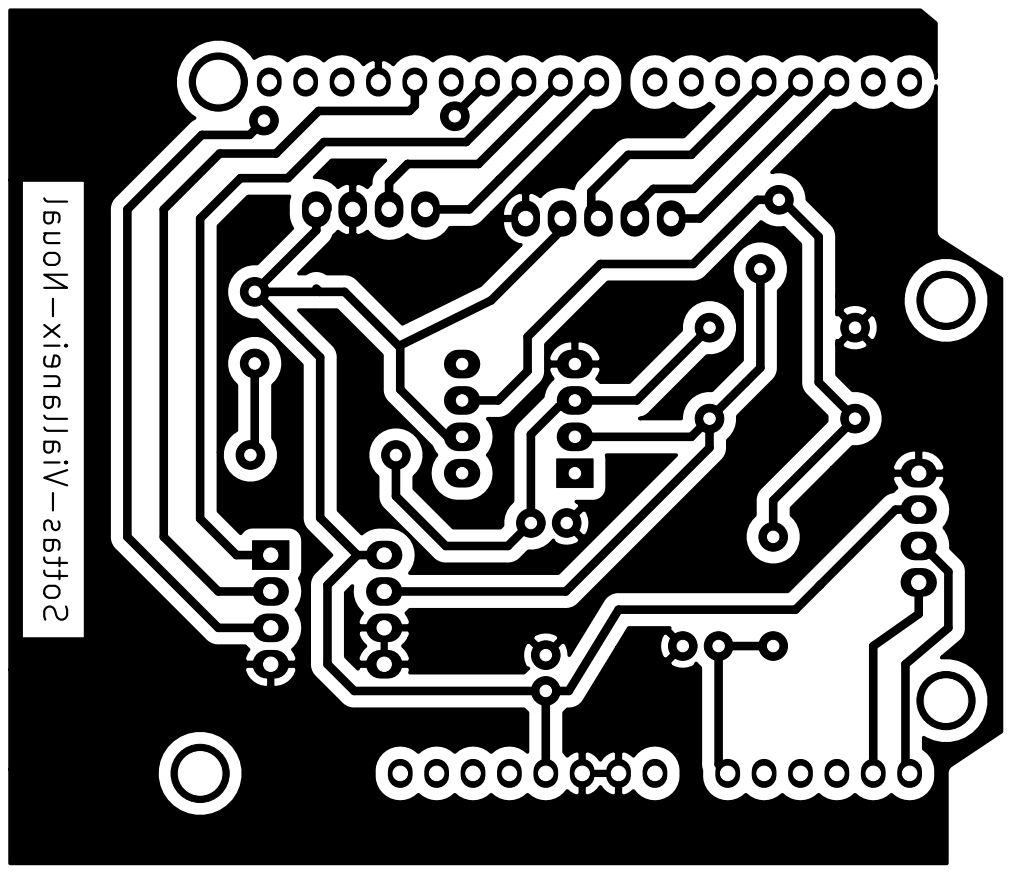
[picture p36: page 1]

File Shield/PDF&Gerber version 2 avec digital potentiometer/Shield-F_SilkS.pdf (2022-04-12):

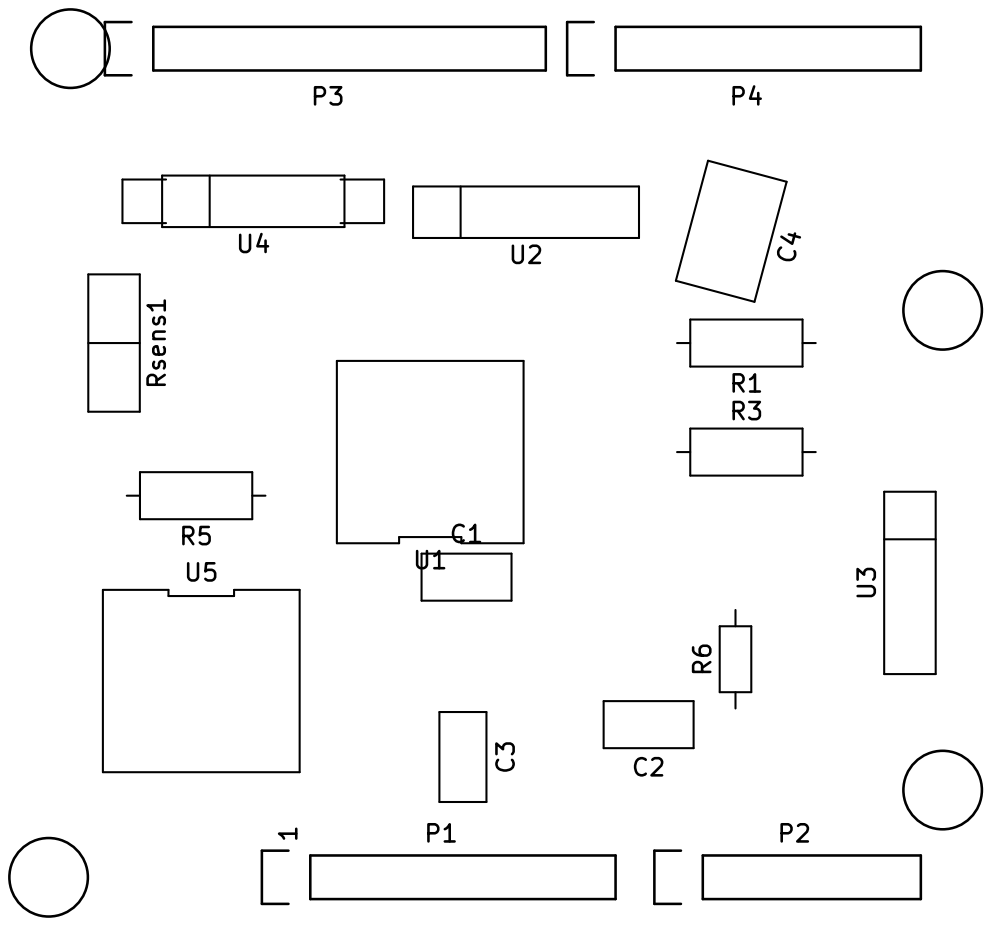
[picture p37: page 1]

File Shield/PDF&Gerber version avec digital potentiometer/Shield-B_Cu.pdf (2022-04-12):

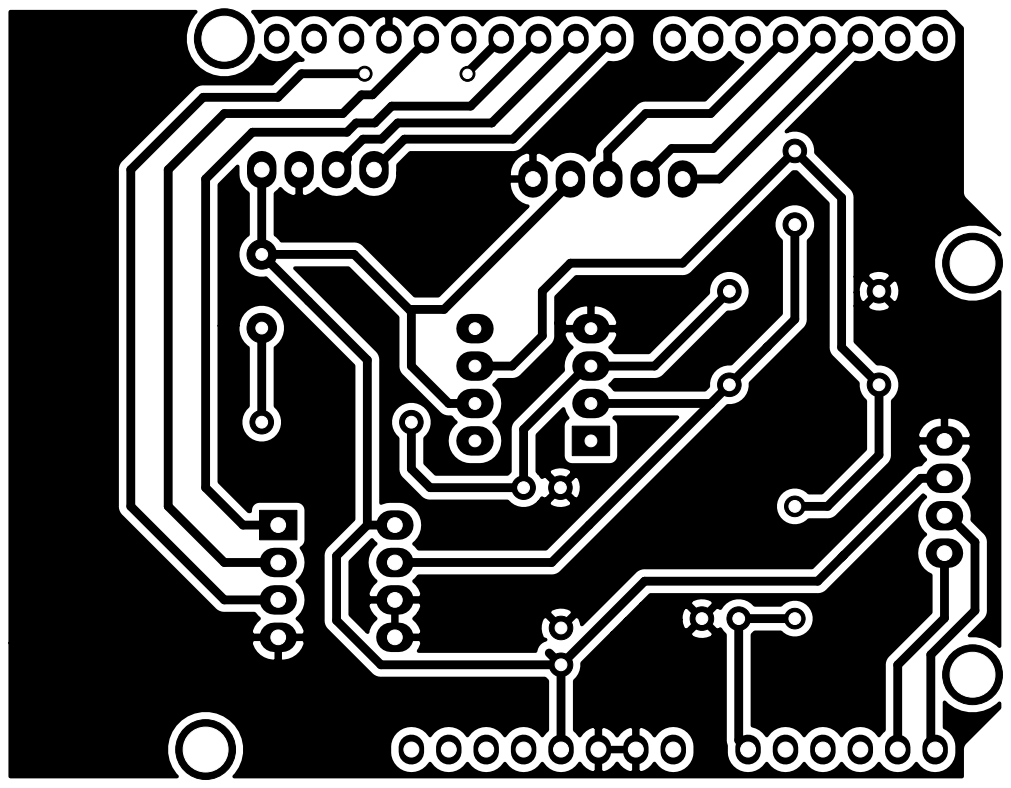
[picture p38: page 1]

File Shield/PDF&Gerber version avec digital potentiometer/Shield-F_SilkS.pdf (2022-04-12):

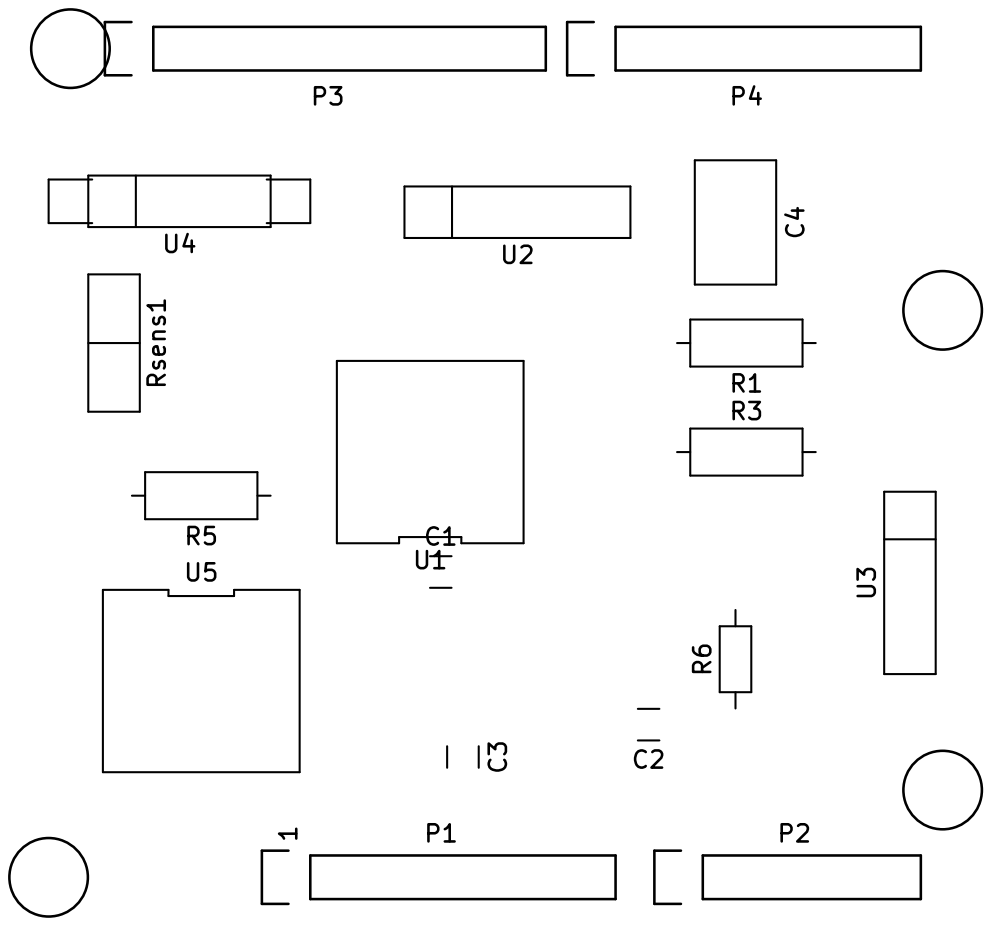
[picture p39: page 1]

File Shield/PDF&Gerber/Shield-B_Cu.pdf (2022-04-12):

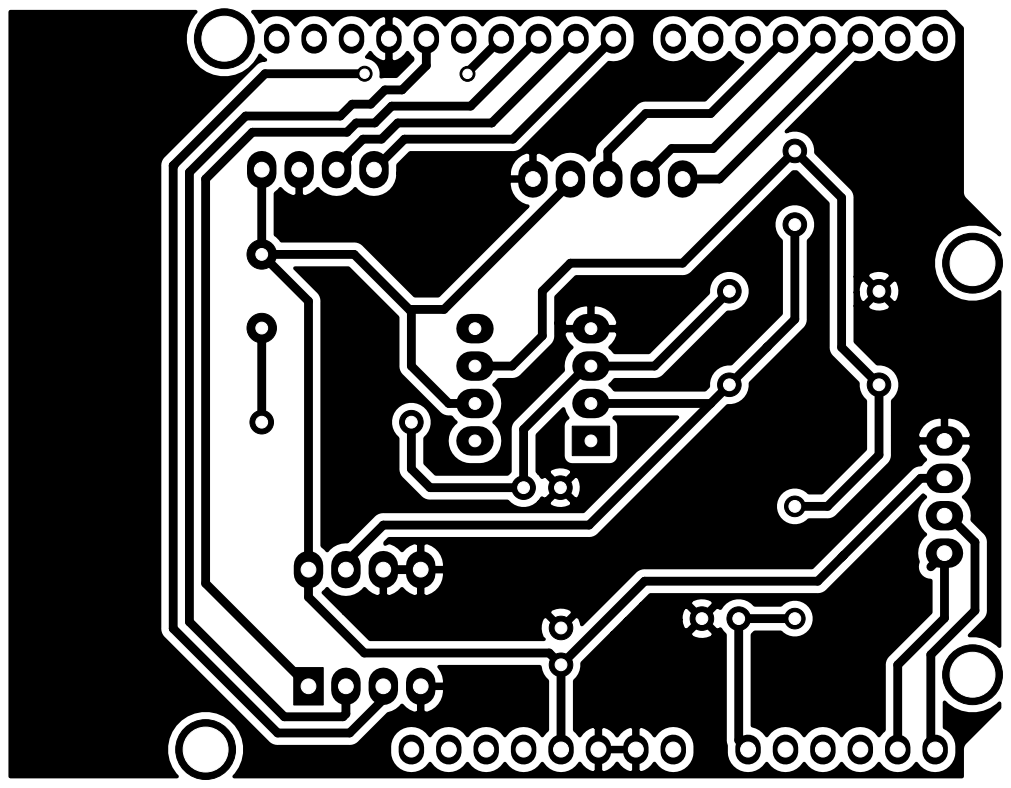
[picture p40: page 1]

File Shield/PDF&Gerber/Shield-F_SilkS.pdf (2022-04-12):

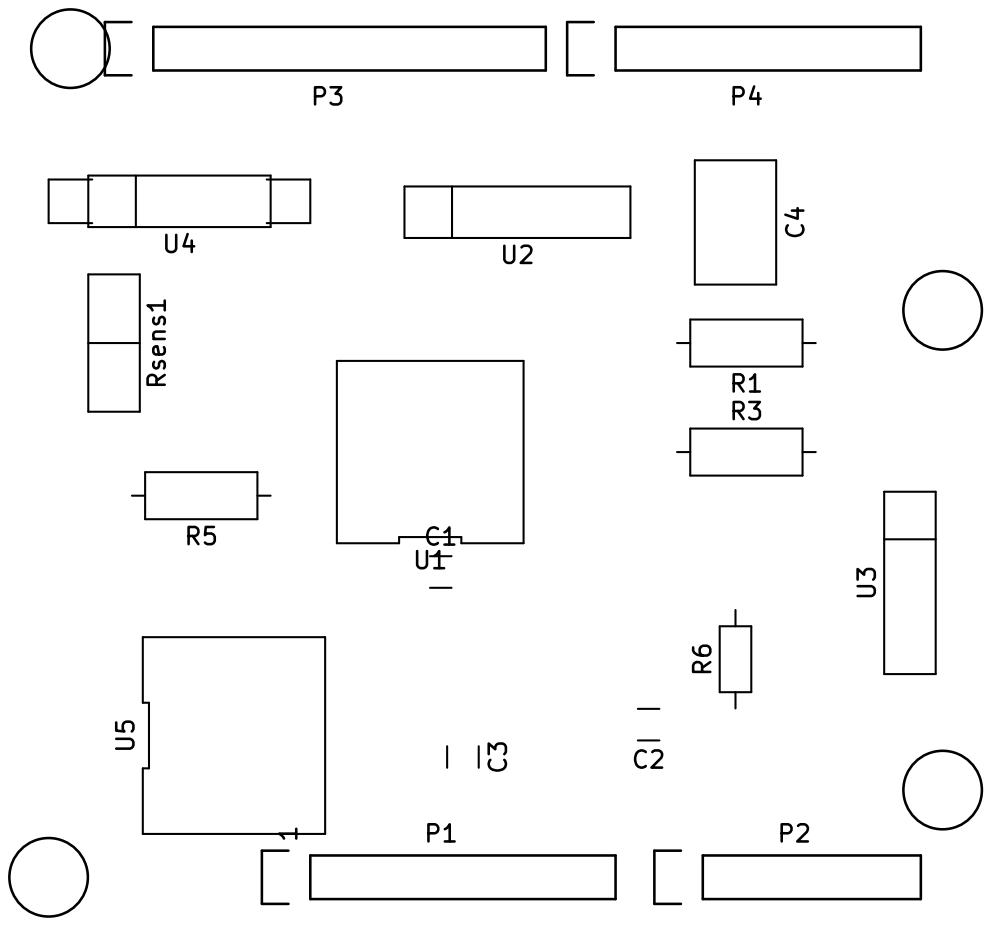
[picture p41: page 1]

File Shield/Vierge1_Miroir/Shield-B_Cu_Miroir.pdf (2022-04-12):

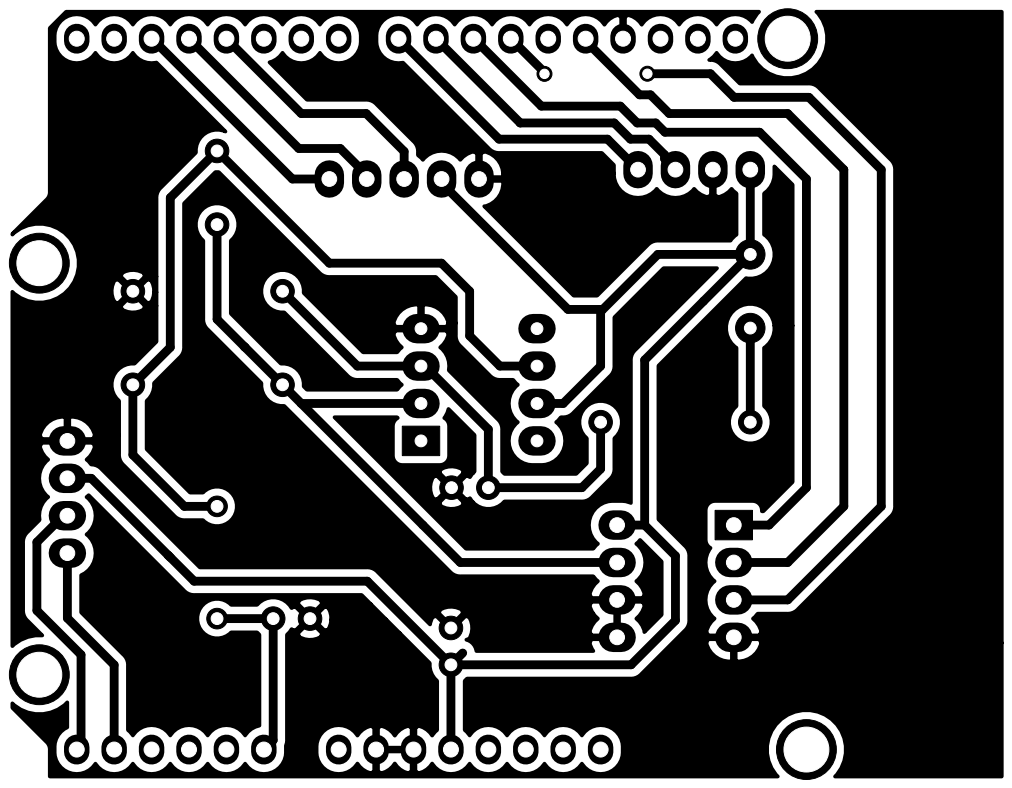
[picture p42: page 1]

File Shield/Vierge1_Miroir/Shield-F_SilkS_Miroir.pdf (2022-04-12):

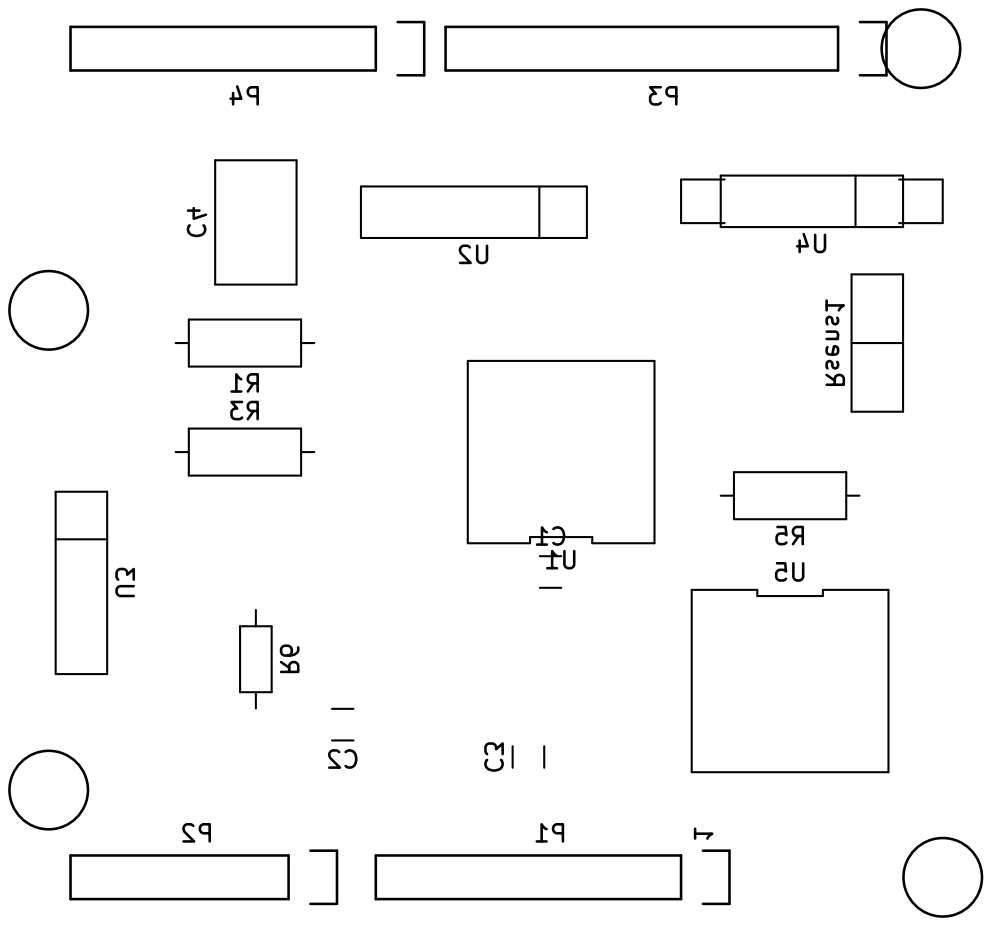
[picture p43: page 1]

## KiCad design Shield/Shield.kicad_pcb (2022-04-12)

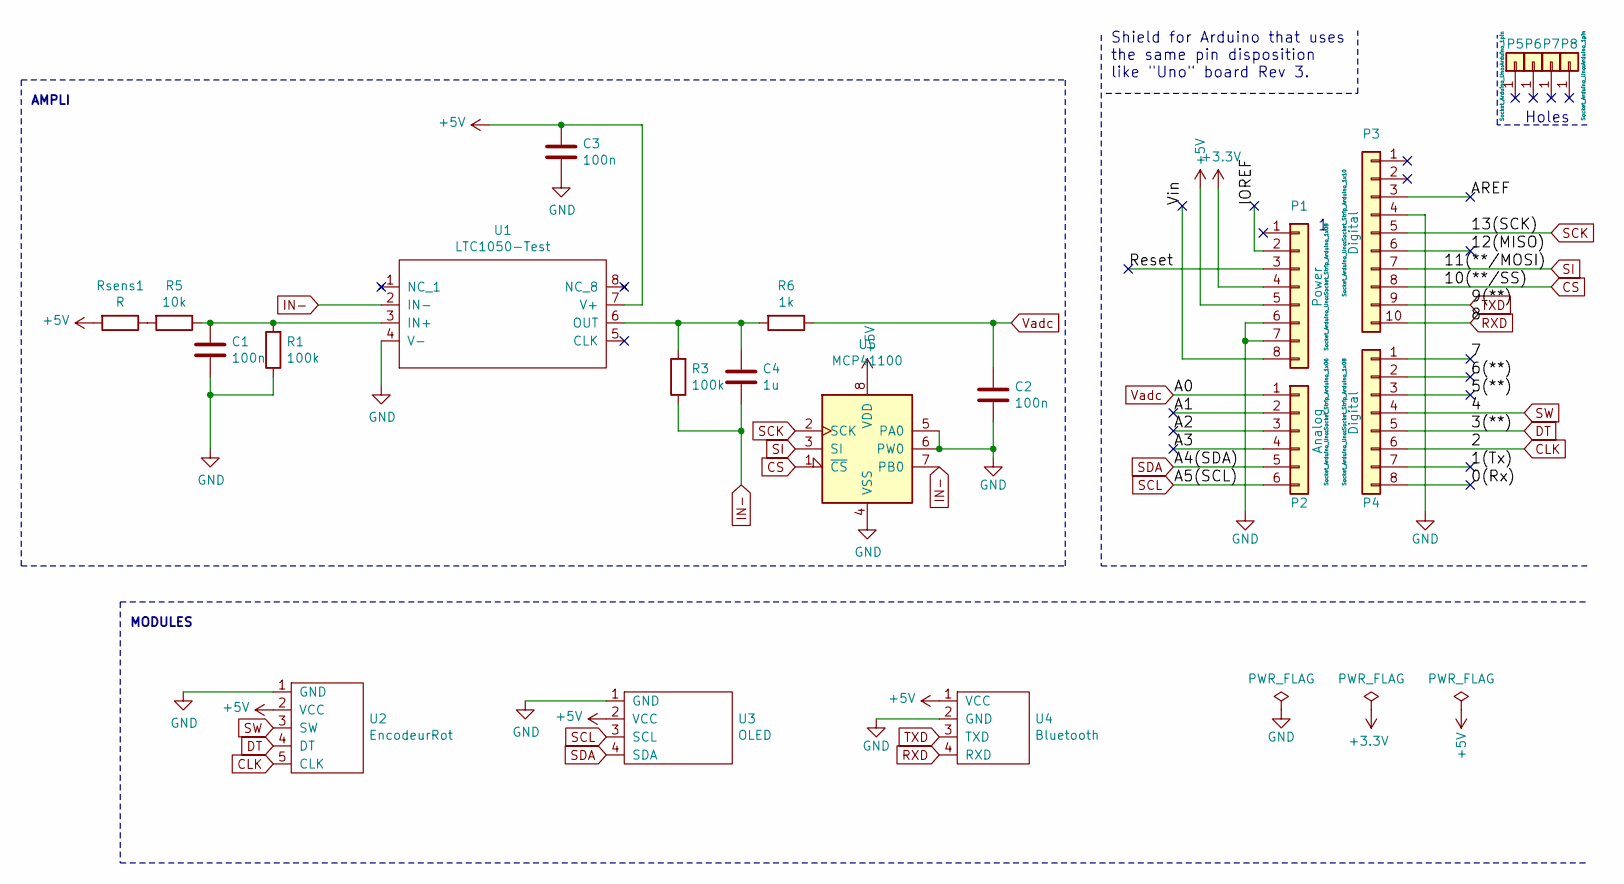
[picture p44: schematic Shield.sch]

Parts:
C1, C2, C3: 100n; C_Disc_D3.0mm_W1.6mm_P2.50mm
C4: 1u; C_Rect_L7.0mm_W4.5mm_P5.00mm
P1: Power; Socket_Strip_Arduino_1x08
P2: Analog; Socket_Strip_Arduino_1x06
P3: Digital; Socket_Strip_Arduino_1x10
P4: Digital; Socket_Strip_Arduino_1x08
P5, P6, P7, P8: CONN_01X01; Arduino_1pin
R1, R3: 100k; R_Axial_DIN0207_L6.3mm_D2.5mm_P10.16mm_Horizontal
R5: 10k; R_Axial_DIN0207_L6.3mm_D2.5mm_P10.16mm_Horizontal
R6: 1k; R_Axial_DIN0204_L3.6mm_D1.6mm_P7.62mm_Horizontal
Rsens1: R; Sensor
U1: LTC1050-Test; LTC1050
U2: EncodeurRot
U3: OLED
U4: Bluetooth
U5: MCP41100

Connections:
+3V3: P1.4
+5V: C3.2, P1.5, Rsens1.2, U1.7 (V+), U2.2 (VCC), U3.2 (VCC), U4.1 (VCC), U5.8 (VDD)
/0(Rx): P4.8
/1(Tx): P4.7
/5(**): P4.3
/6(**): P4.2
/7: P4.1
/12(MISO): P3.6
/A1: P2.2
/A2: P2.3
/A3: P2.4
/AREF: P3.3
/IOREF: P1.2
/Reset: P1.3
/Vin: P1.8
CLK: P4.6, U2.5 (CLK)
CS: P3.8, U5.1 (~CS)
DT: P4.5, U2.4 (DT)
GND: C1.2, C2.2, C3.1, P1.6, P1.7, P3.4, R1.1, U1.4 (V-), U2.1 (GND), U3.1 (GND), U4.2 (GND), U5.4 (VSS), U5.5 (PA0), U5.6 (PW0)
IN-: C4.2, R3.1, U1.2 (IN-), U5.7 (PB0)
unnamed: C1.1, R1.2, R5.1, U1.3 (IN+)
unnamed: C4.1, R3.2, R6.2, U1.6 (OUT)
unnamed: R5.2, Rsens1.1
RXD: P3.10, U4.4 (RXD)
SCK: P3.5, U5.2 (SCK)
SCL: P2.6, U3.3 (SCL)
SDA: P2.5, U3.4 (SDA)
SI: P3.7, U5.3 (SI)
SW: P4.4, U2.3 (SW)
TXD: P3.9, U4.3 (TXD)
Vadc: C2.1, P2.1, R6.1

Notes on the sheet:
Holes
Shield for Arduino that uses the same pin disposition like "Uno" board Rev 3.
AMPLI
MODULES

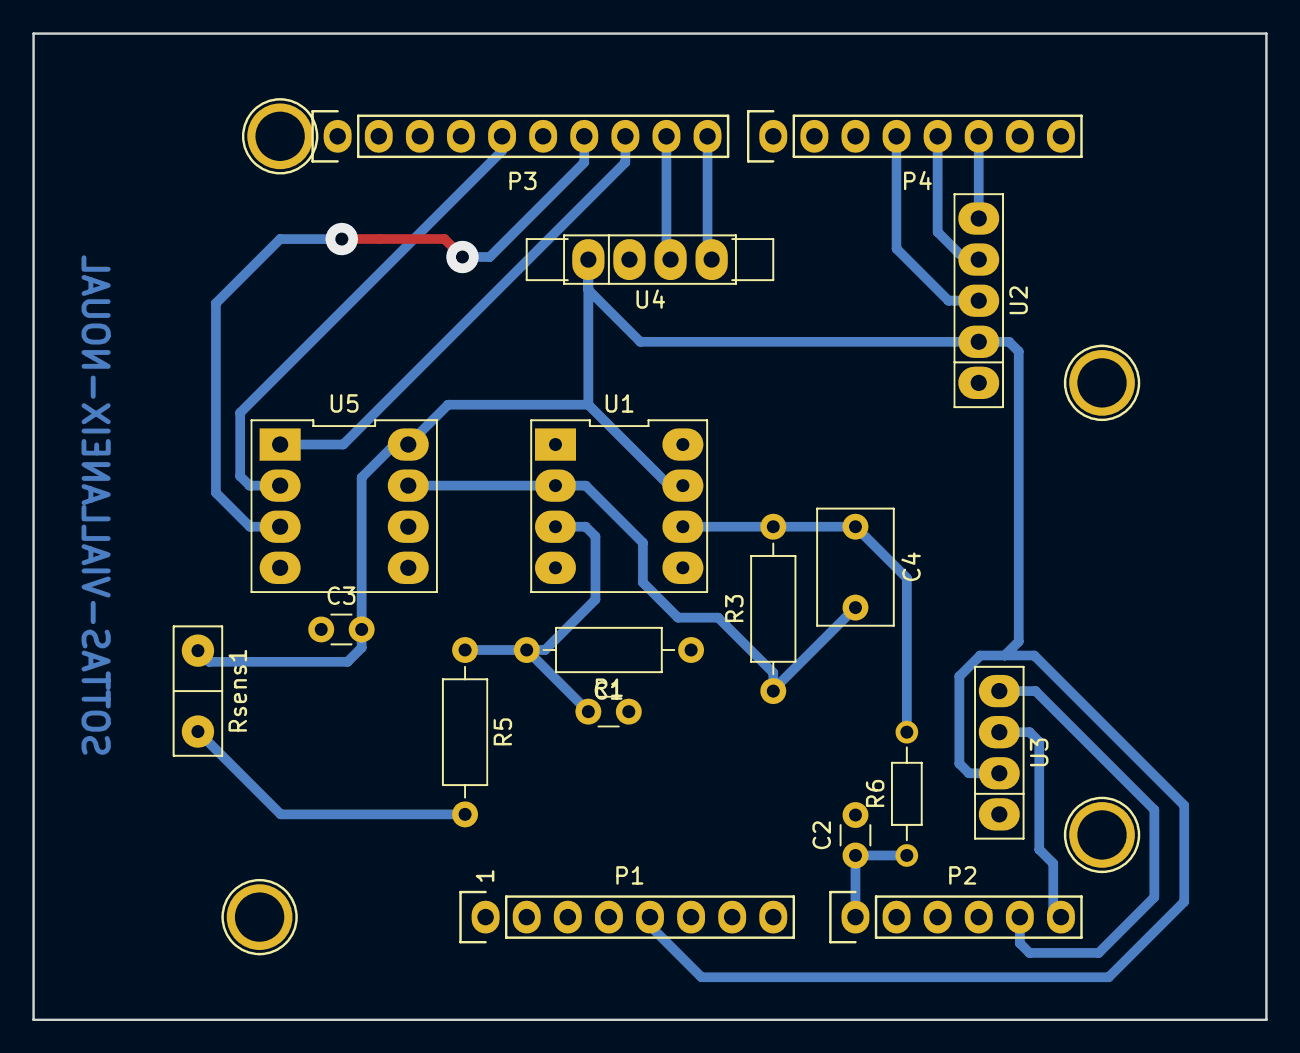
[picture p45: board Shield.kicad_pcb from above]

Board: 2 copper layers, 76.2 x 61.0 mm, 22 parts (0 on the bottom side), 17 nets.

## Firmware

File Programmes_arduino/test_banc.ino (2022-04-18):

//Programme de base : 
//PROJET MOSH - CAPTEUR GRANULOMETRIQUE
//Version 4 - 15/04

#include<Servo.h>


////////////////////  ENCODEUR ROTATOIRE
#define encoder0PinA 2
#define Switch 3
volatile unsigned int encoder0Pos = 0;



////////////////////  POTENTIOMETRE R2
#include <SPI.h>
const byte csPin = 10;
const int maxPositions = 256;
const long rAB = 46300;
const byte rWiper = 125;
const byte pot0 = 0x11;
const byte pot0Shutdown  = 0x21;
long resistanceWB;


////////////////////  OLED
#include <Adafruit_SSD1306.h>
#define nombredDePixelsEnLargeur 128
#define nombredePixelsEnHauteur 64
#define brocheResetOLED -1
#define adresseI2CecranOLED 0x3C
Adafruit_SSD1306 ecranOLED(nombredDePixelsEnLargeur, nombredePixelsEnHauteur, &Wire, brocheResetOLED);


////////////////////  CAPTEUR
int sense = 0;
int potar=100;
int R1=100;
float R2=(((rAB*potar)/maxPositions) + rWiper)/1000;
int R3=100;
int R5=10;
int R6=1;
float Rsensor;


////////////////////  MENU ET NAVIGATION
#define PRINCIPAL 0
#define QUICKSENSE 1
#define SERIALSENSE 2
#define INFOS 3
int clic=1;
int menu=0;
int ligne=0;


////////////////////  BLUETOOTH
#include <SoftwareSerial.h>
#define rxPin 9
#define txPin 8
SoftwareSerial mySerial(rxPin, txPin);


///////////////////// VARIABLES BANC DE TEST

Servo myservo;// create servo object to control a servo
int nbCycles = 5; // nombre de cycles
int Nb=0; // nombre de cycle max choisi par utilisateur encodeur rot.
int iCase = 0; // variable pour le switch case de la fonction cycle()
int x = 0; // incrément de degrés pour banc
int cycleAccomplis = 0;
int deltaTheta = 5;

//////////////////// VARIABLES Flex sensor
const int flexPin = A1;
float Vflex = 0;
const float VCC = 5;
const float R_DIV = 46500.0;
const float flatResistance = 26500.0;//resistance à plat
const float bendResistance = 53000.0; //resistance à 90°


void setup() {
  
  Serial.begin(9600);
  mySerial.begin(9600);


  ////////////////////  BLUETOOTH
  pinMode(rxPin, INPUT);
  pinMode(txPin, OUTPUT);


  ////////////////////  POTENTIOMETRE R2
  digitalWrite(csPin, HIGH);
  pinMode(csPin, OUTPUT);
  SPI.begin();


  ////////////////////  OLED
  if(!ecranOLED.begin(SSD1306_SWITCHCAPVCC, adresseI2CecranOLED))
  {
    while(1);
  }
  ecranOLED.setTextSize(2);
  ecranOLED.setTextColor(SSD1306_WHITE);


  ////////////////////  ENCODEUR ROTATOIRE
  pinMode(encoder0PinA, INPUT);
  digitalWrite(encoder0PinA, HIGH);
  attachInterrupt(0,doEncoder,RISING);
  pinMode(Switch, INPUT_PULLUP);
  attachInterrupt(1,doSwitch,FALLING);

  /////////////////// SETUP BANC DE TEST
  myservo.attach(6); // connexion servo sur pin 6
  pinMode(flexPin, INPUT); //setup flex
  
}




void loop() {

  ////////////////////  INITIALISATION MENU
  clic=1;
  encoder0Pos = 0;
  delay(50);


  ////////////////////  MESURE DE LA TENSION ET ADAPTATION POTENTIOMETRE R2
  float output = analogRead(sense);
  output=output*5/1024;
  Serial.print("Tension mesurée : ");
  Serial.print(output);
  Serial.print(" V");
  
  if(output<0.9)
  {
    potar-=1;
  }
  else if(output>1.1)
  {
    potar+=1;
  }
  
  potar = constrain(potar,0,255);
  setPotWiper(pot0, potar);
  R2 = (((rAB*potar)/maxPositions) + rWiper)/1000;
  Rsensor = ((1+R3/R2)*R1*(5/output)-R1-R5)/1000;
  Serial.print("\t\t\tRsensor : ");
  Serial.print(Rsensor);
  Serial.println(" MOhms");

  
  ////////////////////  MENU ET NAVIGATION
  ecranOLED.clearDisplay();
  ecranOLED.setCursor(0, 0);
  ecranOLED.setTextColor(SSD1306_WHITE);
  
  
  if (menu==PRINCIPAL)
  {
    
    if(encoder0Pos==1)
    {
    if (ligne<2){ligne+=1;}
    else {ligne=0;}
    }
    
    if(ligne==0)
    {
      ecranOLED.setTextColor(SSD1306_BLACK, SSD1306_WHITE);
      ecranOLED.println("MESURE");
      ecranOLED.setTextColor(SSD1306_WHITE);
      ecranOLED.println("REPETITION");
      ecranOLED.println("INFOS");
      if(clic==0){menu=QUICKSENSE;}
    }
    else if(ligne==1)
    {
      ecranOLED.println("MESURE");
      ecranOLED.setTextColor(SSD1306_BLACK, SSD1306_WHITE);
      ecranOLED.println("REPETITION");
      ecranOLED.setTextColor(SSD1306_WHITE);
      ecranOLED.println("INFOS");
      if(clic==0){
        menu=SERIALSENSE;
        Nb=0;
      }
    }
    else
    {
      ecranOLED.println("MESURE");
      ecranOLED.println("REPETITION");
      ecranOLED.setTextColor(SSD1306_BLACK, SSD1306_WHITE);
      ecranOLED.println("INFOS");
      if(clic==0){menu=INFOS;}
    }
  }

  else if (menu==QUICKSENSE)
  {
    ecranOLED.println("Output : ");
    ecranOLED.print(output);
    ecranOLED.println(" V");
    ecranOLED.println("Rsensor : ");
    ecranOLED.print((int) Rsensor);
    ecranOLED.print(" MOhms");
    mySerial.print((int) Rsensor);
    while(mySerial.available())
    {
      Serial.print((char) mySerial.read());
    }
    if(clic==0){menu=PRINCIPAL;}
  }

  else if (menu==SERIALSENSE)
  {
    if(encoder0Pos==1)
    {
      Nb+=1;
    }
    ecranOLED.println("Mode Cycle");
    ecranOLED.println("Nombre de");
    ecranOLED.print("mesures : ");
    ecranOLED.print(Nb);
    //MesureFlexSensor();
    //cycle(); //
    if(clic==0){menu=PRINCIPAL;}
  }
  
  else if (menu==INFOS)
  {
    ecranOLED.setTextColor(SSD1306_BLACK, SSD1306_WHITE);
    ecranOLED.println("Capteur V4");
    ecranOLED.setTextColor(SSD1306_WHITE);
    ecranOLED.println("Sottas,");
    ecranOLED.println("Noual,");
    ecranOLED.println("Viallaneix");
    if(clic==0){menu=PRINCIPAL;}
  }

  
  ecranOLED.display();
}




////////////////////  POTENTIOMETRE R2
void setPotWiper(int addr, int pos)
{
  digitalWrite(csPin,LOW);
  SPI.transfer(addr);
  SPI.transfer(pos);
  digitalWrite(csPin, HIGH);
  
  resistanceWB = ((rAB*pos)/maxPositions) + rWiper;
  Serial.print("\t\t\tPosition sur 256 : ");
  Serial.print(pos);
  Serial.print("\t\t\tR2 : ");
  Serial.print(resistanceWB);
  Serial.print(" Ohms");
}



////////////////////  ENCODEUR ROTATOIRE POUR LE CLIC
void doSwitch()
{
  static unsigned long tempsprecedent = 0;
  unsigned long temps = millis();
  if (temps - tempsprecedent > 100) 
  {
    clic = 0;
  }
  tempsprecedent=temps;
}


////////////////////  ENCODEUR ROTATOIRE POUR LA ROTATION
void doEncoder()
{
  encoder0Pos=1;
}


////////////////////  FONCTIONS BANC DE TEST //////////////////////////
void cycle() {
  
  switch (iCase) {
    case 0:
      x = x + 1;
      myservo.write(x);
      Serial.print(cycleAccomplis);
      Serial.print("\t theta : ");
      Serial.print(x-90);
      Serial.println(" degrés\t");
      Serial.print(Rsensor);
      Serial.print(" MOhms");
        if (x >= ((90-deltaTheta)*2)) {iCase = 1;} // 
     //return x;
      break;
    case 1:
      x = x - 1;
      myservo.write(x-deltaTheta);
      Serial.print(cycleAccomplis);
      Serial.print("\t theta : ");
      Serial.print(x-deltaTheta);
      Serial.println(" degrés");
        if (x <= 0) {
          iCase = 0;
          cycleAccomplis += 1;}
        if (nbCycles = Nb){
          iCase = 2;
        }
       break;
    case 2:
       break;
    default:
      break;
  }
}

void MesureFlexSensor() {

  //Flex
 int ADCflex = analogRead(flexPin);
 float Vflex = ADCflex * VCC /1023.0;
 float Rflex = R_DIV * (VCC / Vflex -1.0);
 Serial.println("resistance : " + String(Rflex) + "ohms");
 float angle = map(Rflex, flatResistance, bendResistance, 0, 90);
 Serial.println("Bend : " + String(angle) + " degrés");
 }

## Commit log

2022-04-06 Create KiCad files
    Fichiers servant à la réalisation du PCB
2022-04-06 KiCAD PCB
2022-04-08 Modification du programme : Pin B de l'encodeur supprimée et pin 4 du switch basculé sur pin 3 pour gérer les 2 interrupt dispo en 2 et 3.
2022-04-12 Ajout folders Shield & Images
    [4-Pin Header - Female - 2.54mm.step, KY-040 Rotary Encoder.STEP, Shield-B_Cu.gbr, Shield-F_SilkS.gbr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]
2022-04-16 Création Dossier PCB
2022-04-16 bis creation dossier PCB
2022-04-16 Images de l'apk par Léo
2022-04-16 ajout programmes banc de test
2022-04-16 Images de l'application par Léo
2022-04-16 Programme Sans banc de test
2022-04-16 Version html de l'analyse MSA
2022-04-17 Create PCB
2022-04-17 Ajout Images/PCB/
2022-04-18 Blocs de l'application sur MitAppInventor
2022-04-18 Face avant de l'application
2022-04-18 Version finale de l'arduino
